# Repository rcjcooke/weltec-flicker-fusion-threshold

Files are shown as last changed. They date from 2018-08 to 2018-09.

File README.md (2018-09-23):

# weltec-flicker-fusion-threshold

Weltec MG7013 Project 0 - Teensy based human flicker fusion threshold determining system.

>"The flicker fusion threshold (or flicker fusion rate) is a concept in the psychophysics of vision. It is defined as the frequency at which an intermittent light stimulus appears to be completely steady to the average human observer."

*Flicker fusion threshold - Wikipedia. (n.d.). Retrieved March 15, 2017, from https://www.wikipedia.com/en/Flicker_fusion_threshold*

The implementation of the system to test this allows the user to adjust a potentiometer to increase or decrease the "flicker rate", the frequency, of an LED blinking on and off. The duty cycle of the flicker is always 50%. The system is designed to allow the user to vary the frequency between 25 and 100 Hz. When the user has determine the point at which they can *just* see a steady state of the LED a button is pressed which tells the user the frequency over a serial interface (USB: 115200 / 8N1).

## Design / Assembly
The design process itself was simple. From a hardware perspective it was clear what was required and from a software perspective it was simply a case of pulling together some button debouncing code, some ADC access code and using the system timer to drive the LED output frequency.  

### Components / BoM
| Supplier | Supplier Part # | # | Description       | MNF Part # |
|:---------|:---------------:|---|:------------------|:-----------|
|          |                 | 1 | Teensy 3.2        |            |
|          |                 | 1 | LED               |            |
|          |                 | 1 | 10k Potentiometer |            |
|          |                 | 1 | 330Ohm Resistor   |            |

**Note**: 330Ohm resistor for current limiting the LED. The Teensy supplies 3.3V on its GPIO pins and allows a maximum current draw of 25mA (ST Microelectronics, 2016). The LED is an unknown quantity so the max forward current is unknown as is it's voltage drop. Based on an assumed voltage drop of 2V (given it's a green LED), R = (Vs - Vf) / I = (3.3-2)/0.025 = 52 Ohms. But given we don't actually know, let's assume no voltage drop across the LED then this would give us 132 Ohm. A safety (and what was available in the box :) ) leaves us with a 330 Ohm resistor.

### Electronics
The components were wired up on breadboard as per the diagram below.

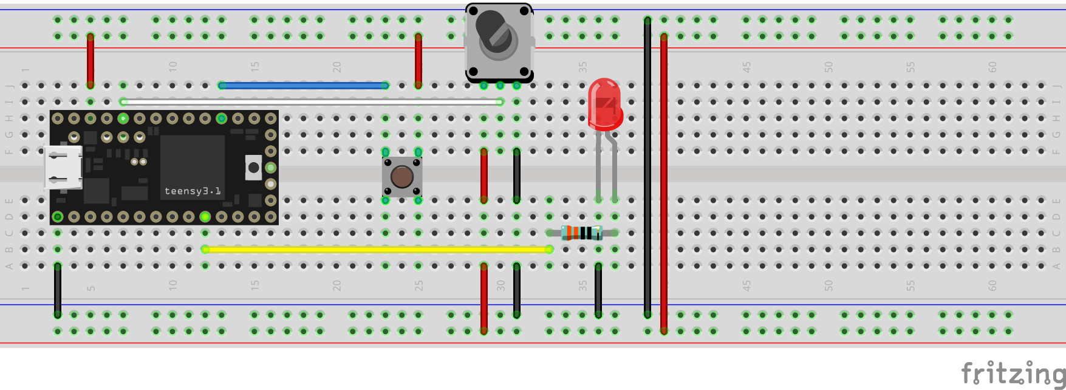
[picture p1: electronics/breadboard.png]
Breadboard image


**Note**: It would appear that Fritzing's Teensy package has the VIN and 3.3V pins switched which is particularly frustrating when trying to get the schematic put together correctly. This is my first time using Fritzing so I haven't investigated this further.

The schematic was drawn up in Eagle as follows:

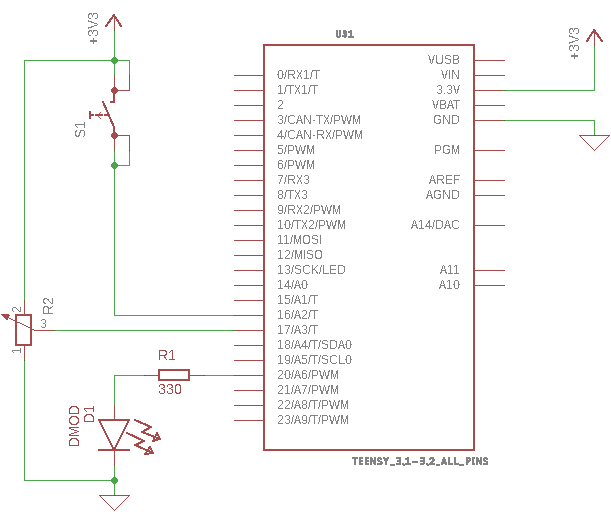
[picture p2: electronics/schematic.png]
Schematic image


### Software

The code has been written to work with the Teensy 3.2 Arduino framework. This is slightly upgraded from the standard Arduino framework and provides "fast" versions of digitalRead for example. This has been taken advantage of on writing the interrupt routine that handles button presses so as not to significantly impede the execution of the interrupt routine which implements a software debounce of the button.

For interest the codebase was also adapted to work on the ESP32 Arduino framework so that debug facilities could be tested on the ESP32 Wrover Kit development board. There are again some subtle variations for the ESP32 implementation of the Arduino framework and these required the addition of a number of preprocessor directives to handle them.

**Note**: The default in platformio.ini is currently set to Teensy. Simply replace the `env_default = teensy31` with `env_default = esp-wrover-kit` to change the default to build and deploy to the ESP32 board instead.

## Results

Serial output looks like the following:

`Flicker fusion threshold frequency: 52.95Hz`<br>
`Flicker fusion threshold frequency: 52.95Hz`<br>
`Flicker fusion threshold frequency: 89.51Hz`<br>
`Flicker fusion threshold frequency: 37.93Hz`<br>
`Flicker fusion threshold frequency: 25.00Hz`<br>
`Flicker fusion threshold frequency: 100.00Hz`<br>
`Flicker fusion threshold frequency: 44.29Hz`<br>
`Flicker fusion threshold frequency: 48.72Hz`<br>

As can be seen, the frequency varies between 25 Hz and 100 Hz.

The calculated frequency output was tested against reality and found to be accurate to within ~0.2Hz. This can be seen in the oscillogram below:

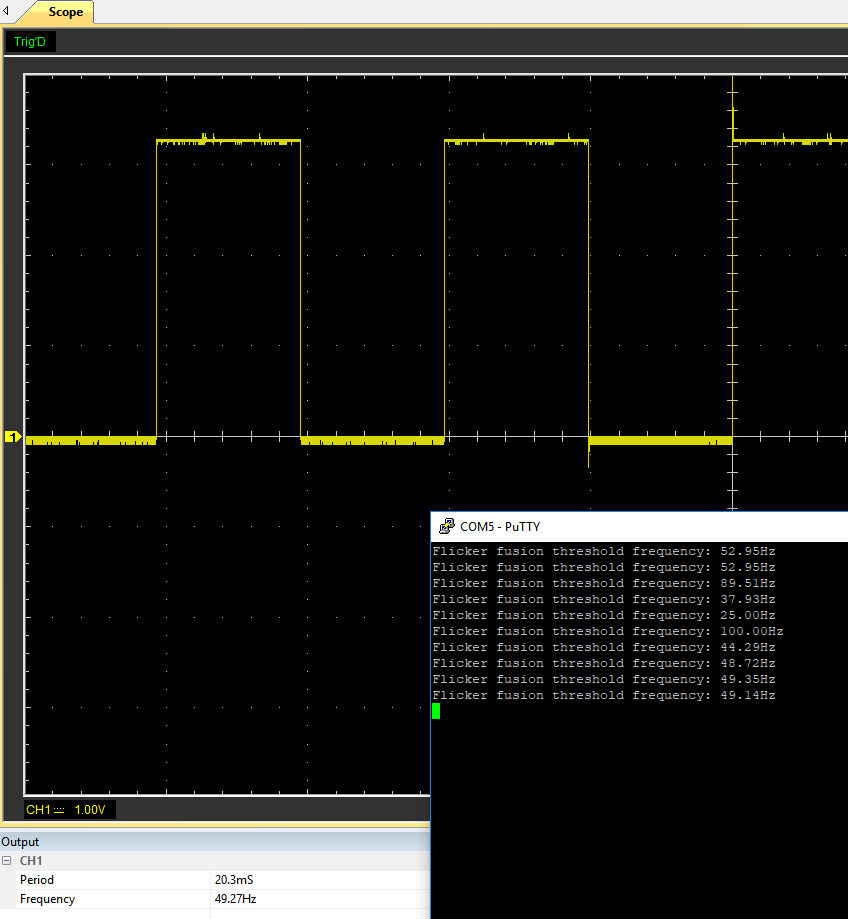
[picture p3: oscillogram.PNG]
LED frequency oscillogram


## Conclusions
It turns out that my threshold is between about 49 and 53 Hz depending on ambient lighting conditions and how directly I'm looking at the LED. Interestingly, I believe it might be lower with a blue LED which I was experimenting with on the ESP32. Further investigation into whether the wavelength affects this phenomenon is warranted given further time.

Given the realisation that ambient lighting conditions have some affect, future experiments should be conducted in a consistently lit, probably dark, environment.

## Update
Since the first cut of this I have also rebuilt this on an ESP Wrover Kit (based on the ESP32 Wroom chip) and added a 7-segment display to show the frequency so that the user doesn't have to fire up a Terminal to find out. The resulting setup can be seen below:

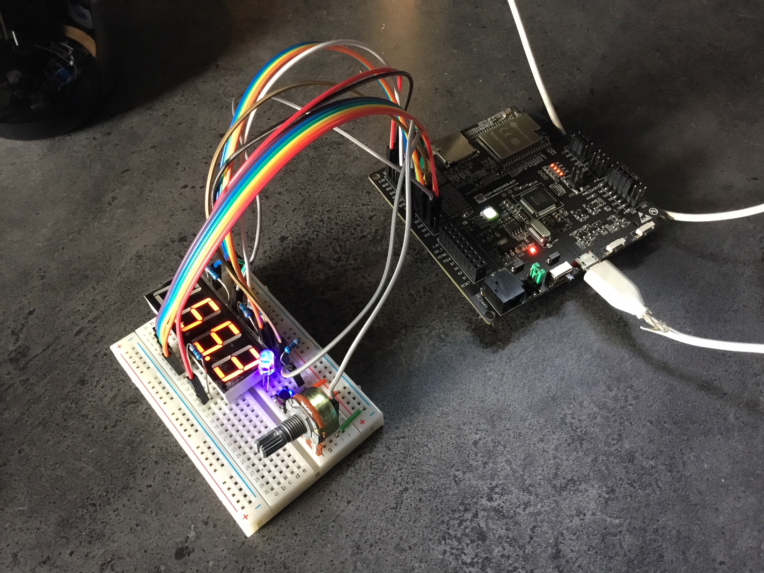
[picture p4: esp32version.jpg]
ESP Wrover Kit based implementation


In putting this together I found a frustrating lack of consolidated information about the ESP Wrover Kit board pinout so I've created a pinout map for it which can be found in the datasheets directory. I couldn't connect up one of the pins for the 4 digit 7-segment display in the end because I didn't have enough GPIO available with the setup that the wrover kit dev board uses (though in theory it's alterable with a little surgery). Also this is because I wanted the JTAG interface available, which steals some additional GPIO when it's enabled. Another couple of pins are used by the 32 KHz crystal on the board. Finally some are input only. Details can be found in the spreadsheet.

Secondly the button I used happen to be WAY more bouncy than the one I used on the Teensy so I had to increase the lockout to 100 ms (instead of only 2ms!). Works nicely now though. There are a number of other quirks of the Arduino framework implementation of the ESP32 I discovered along the way, which can be found in the codebase.

## References

**Note**: Some relevent datasheets can be found in the datasheets directory of this repository.

1. PJRC. (2018, August 24). Teensy 3.2 & 3.1: New Features. Retrieved from pjrc.com: https://www.pjrc.com/teensy/teensy31.html#specs
2. ST Microelectronics. (2016, September). STM32F415xx datasheet - production data; ARM Cortex-M4 32b MCU+FPU, 210DMIPS, up to 1MB Flash/192+4KB RAM, crypto, USB OTG HS/FS, Ethernet, 17 TIMs, 3 ADCs, 15 comm. interfaces & camera.

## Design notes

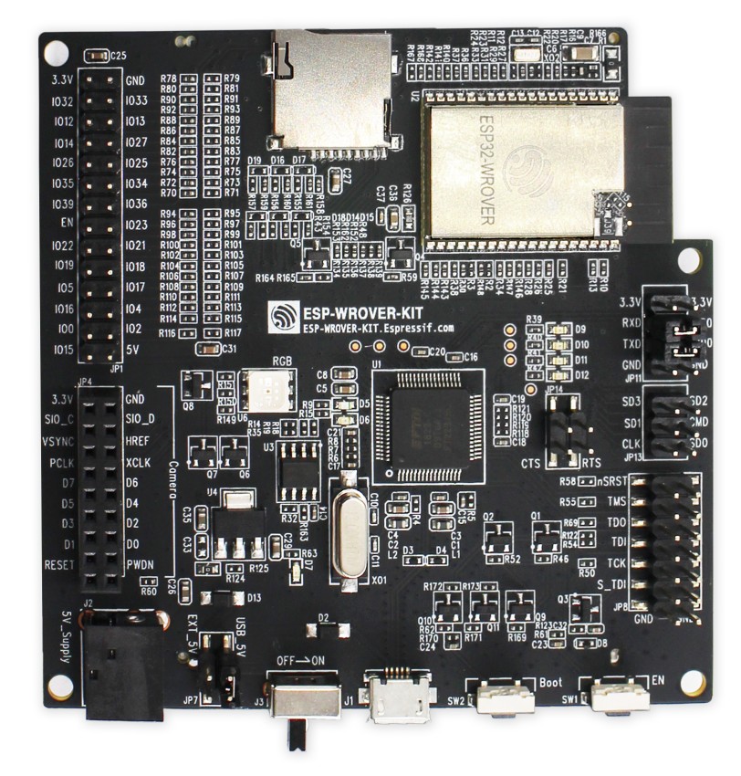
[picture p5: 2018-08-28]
datasheets/esp-wrover-kit-v3.jpg

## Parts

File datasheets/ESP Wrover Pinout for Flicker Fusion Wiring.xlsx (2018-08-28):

 |  |  |  |  |  |  |  |  |  |  |  | # = Number
 |  |  |  |  |  |  |  |  |  |  |  | T = Type |  | SPI01 | SPI2 | SPI3
 |  |  |  |  |  |  |  |  |  |  |  | GPIO | RTC GPIO | DAC
 |  |  |  |  |  |  |  |  |  |  |  | ADC1 | ADC2 | EMAC
 |  |  |  |  |  |  |  |  |  |  |  | TOUCH |  | SDIO Slave
 |  |  |  |  |  |  |  |  |  |  |  | Clock |  | SDIO Host Port 1 | SDIO Host Port 2
 |  |  |  |  |  |  |  |  |  |  |  |  |  | JTAG
 |  |  |  |  |  |  |  |  |  |  |  |  |  | UART0 | UART1 | UART2
 |  | T | # | Name | Silk | Silk | Name | # | T
 |  | P | 2 | 3V3 | 3.3V | GND | GND | 1 | P
 | XTAL_32K_P | I/O | 8 | IO32 | IO32 | IO33 | IO33 | 9 | I/O | XTAL_32K_N
 | MTDI | I/O | 14 | IO12 | IO12 | IO13 | IO13 | 16 | I/O | MTCK
 | MTMS | I/O | 13 | IO14 | IO14 | IO27 | IO27 | 12 | I/O | GPIO27 | 7-Seg-Display E
7-Seg-Display B | GPIO26 | I/O | 11 | IO26 | IO26 | IO25 | IO25 | 10 | I/O | GPIO25 | 7-Seg-Display D
 |  | I | 7 | IO35 | IO35 | IO34 | IO34 | 6 | I | GPIO34 | Button input pin
 |  | I | 5 | SENSOR_VN | IO39 | IO36 | SENSOR_VP | 4 | I | ADC1_CH0 | Potentiometer input pin
 |  | I | 3 | EN | EN | IO23 | IO23 | 37 | I/O | GPIO23 | 7-Seg-Display DP
7-Seg-Display A | GPIO22 | I/O | 36 | IO22 | IO22 | IO21 | IO21 | 33 | I/O | GPIO21 | 7-Seg-Display C
7-Seg-Display 2 | GPIO19 | I/O | 31 | IO19 | IO19 | IO18 | IO18 | 30 | I/O | GPIO18 | LED output pin
7-Seg-Display 3 | GPIO5 | I/O | 29 | IO5 | IO5 | IO17 | Connected to Integrated PSRAM
 |  |  |  | Connected to Integrated PSRAM | IO16 | IO4 | IO4 | 26 | I/O | GPIO4 | 7-Seg-Display G
7-Seg-Display F |  | I/O | 25 | IO0 | IO0 | IO2 | IO2 | 24 | I/O | GPIO2 | 7-Seg-Display 4
 | MTDO | I/O | 23 | IO15 | IO15 | 5V
 |  |  |  |  | JP1

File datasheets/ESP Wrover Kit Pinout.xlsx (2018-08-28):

 |  |  |  |  |  |  |  |  |  |  |  |  |  |  |  |  |  |  |  |  |  |  |  |  |  | # = Number
 |  |  |  |  |  |  |  |  |  |  |  |  |  |  |  |  |  |  |  |  |  |  |  |  |  | T = Type |  | SPI01 | SPI2 | SPI3
 |  |  |  |  |  |  |  |  |  |  |  |  |  |  |  |  |  |  |  |  |  |  |  |  |  | GPIO | RTC GPIO | DAC
 |  |  |  |  |  |  |  |  |  |  |  |  |  |  |  |  |  |  |  |  |  |  |  |  |  | ADC1 | ADC2 | EMAC
 |  |  |  |  |  |  |  |  |  |  |  |  |  |  |  |  |  |  |  |  |  |  |  |  |  | TOUCH |  | SDIO Slave
 |  |  |  |  |  |  |  |  |  |  |  |  |  |  |  |  |  |  |  |  |  |  |  |  |  | Clock |  | SDIO Host Port 1 | SDIO Host Port 2
 |  |  |  |  |  |  |  |  |  |  |  |  |  |  |  |  |  |  |  |  |  |  |  |  |  |  |  | JTAG
 |  |  |  |  |  |  |  |  |  |  |  |  |  |  |  |  |  |  |  |  |  |  |  |  |  |  |  | UART0 | UART1 | UART2
 |  |  |  |  |  |  |  |  | T | # | Name | Silk | Silk | Name | # | T
 |  |  |  |  |  |  |  |  | P | 2 | 3V3 | 3.3V | GND | GND | 1 | P
 |  |  |  | XTAL_32K_P | TOUCH9 | ADC1_CH4 | RTC_GPIO9 | GPIO32 | I/O | 8 | IO32 | IO32 | IO33 | IO33 | 9 | I/O | GPIO33 | RTC_GPIO8 | ADC1_CH5 | TOUCH8 | XTAL_32K_N
MTDI | SD_DATA2 | HS2_DATA2 | HSPIQ | EMAX_TXD3 | TOUCH5 | ADC2_CH5 | RTC_GPIO15 | GPIO12 | I/O | 14 | IO12 | IO12 | IO13 | IO13 | 16 | I/O | GPIO13 | RTC_GPIO14 | ADC2_CH4 | TOUCH4 | EMAC_RX_ER | HSPID | HS2_DATA3 | SD_DATA3 | MTCK
MTMS | SD_CLK | HS2_CLK | HSPICLK | EMAX_TXD2 | TOUCH6 | ADC2_CH6 | RTC_GPIO16 | GPIO14 | I/O | 13 | IO14 | IO14 | IO27 | IO27 | 12 | I/O | GPIO27 | RTC_GPIO17 | ADC2_CH7 | TOUCH7 | EMAC_RX_DV
 |  |  |  | EMAC_RXD1 | DAC_2 | ADC2_CH9 | RTC_GPIO7 | GPIO26 | I/O | 11 | IO26 | IO26 | IO25 | IO25 | 10 | I/O | GPIO25 | RTC_GPIO6 | ADC2_CH8 | DAC_1 | EMAC_RXD0
 |  |  |  |  |  | ADC1_CH7 | RTC_GPIO5 | GPIO35 | I | 7 | IO35 | IO35 | IO34 | IO34 | 6 | I | GPIO34 | RTC_GPIO4 | ADC1_CH6
 |  |  |  |  |  | ADC1_CH3 | RTC_GPIO3 | GPIO39 | I | 5 | SENSOR_VN | IO39 | IO36 | SENSOR_VP | 4 | I | GPIO36 | RTC_GPIO0 | ADC1_CH0
 |  |  |  |  |  |  |  |  | I | 3 | EN | EN | IO23 | IO23 | 37 | I/O | GPIO23 |  |  |  |  | VSPID | HS1_STROBE
 |  |  | VSPIWP | EMAC_TXD1 |  |  | U0RTS | GPIO22 | I/O | 36 | IO22 | IO22 | IO21 | IO21 | 33 | I/O | GPIO21 |  |  |  | EMAC_TX_EN | VSPIHD
 |  |  | VSPIQ | EMAC_TXD0 |  |  | U0CTS | GPIO19 | I/O | 31 | IO19 | IO19 | IO18 | IO18 | 30 | I/O | GPIO18 |  |  |  |  | VSPICLK | HS1_DATA7
 |  | HS1_DATA6 | VSPICS0 | EMAC_RX_CLK |  |  |  | GPIO5 | I/O | 29 | IO5 | IO5 | IO17 | Connected to Integrated PSRAM
 |  |  |  |  |  |  |  |  |  |  | Connected to Integrated PSRAM | IO16 | IO4 | IO4 | 26 | I/O | GPIO4 | RTC_GPIO10 | ADC2_CH0 | TOUCH0 | EMAC_TX_ER | HSPIHD | HS2_DATA1 | SD_DATA1
 |  |  | CLK_OUT1 | EMAC_TX_CLK | TOUCH1 | ADC2_CH1 | RTC_GPIO11 | GPIO0 | I/O | 25 | IO0 | IO0 | IO2 | IO2 | 24 | I/O | GPIO2 | RTC_GPIO12 | ADC2_CH2 | TOUCH2 |  | HSPIWP | HS2_DATA0 | SD_DATA0
MTDO | SD_CMD | HS2_CMD | HSPICS0 | EMAC_RXD3 | TOUCH3 | ADC2_CH3 | RTC_GPIO13 | GPIO15 | I/O | 23 | IO15 | IO15 | 5V
 |  |  |  |  |  |  |  |  |  |  |  | JP1
 |  |  |  |  |  |  |  |  |  |  |  | 3.3V | GND
 |  |  |  |  |  |  |  |  |  |  |  | SIO_C | SIO_D
 |  |  |  |  |  |  |  |  |  |  |  | VSYNC | HREF
 |  |  |  |  |  |  |  |  |  |  |  | PCLK | XCLK
 |  |  |  |  |  |  |  |  |  |  |  | D7 | D6
 |  |  |  |  |  |  |  |  |  |  |  | D5 | D4
 |  |  |  |  |  |  |  |  |  |  |  | D3 | D2
 |  |  |  |  |  |  |  |  |  |  |  | D1 | D0
 |  |  |  |  |  |  |  |  |  |  |  | RESET | PWDN
 |  |  |  |  |  |  |  |  |  |  |  | JP4
 |  |  |  |  |  |  |  |  |  |  |  | 3.3V | 3.3V
 |  |  |  |  |  |  |  |  |  |  |  | RXD | TXD0 | TXD0 | 35 | I/O | GPIO1 | CLK_OUT3 |  | EMAC_RXD2 | U0TXD
 |  |  |  |  |  |  |  |  |  |  |  | TXD | RXD0 | RXD0 | 34 | I/O | GPIO3 | CLK_OUT2 |  |  | U0RXD
 |  |  |  |  |  |  |  |  |  |  |  | GND | GND
 |  |  |  |  |  |  |  |  |  |  |  | JP11
 |  |  |  | U1TXD | HS1_DATA3 | SPIWP | SD_DATA3 | GPIO10 | I/O | 18 | SWP/SD3 | SD3 | SD2 | SHD/SD2 | 17 | I/O | GPIO9 | SD_DATA2 | SPIHD | HS1_DATA2 | U1RXD
 |  |  |  | U2CTS | HS1_DATA1 | SPID | SD_DATA1 | GPIO8 | I/O | 22 | SDI/SD1 | SD1 | CMD | SCS/CMD | 19 | I/O | GPIO11 | SD_CMD | SPICS0 | HS1_CMD | U1RTS
 |  |  |  | U1CTS | HS1_CLK | SPICLK | SD_CLK | GPIO6 | I/O | 20 | SCK/CLK | CLK | SD0 | SDO/SD0 | 21 | I/O | GPIO7 | SD_DATA0 | SPIQ | HS1_DATA0 | U2RTS
 |  |  |  |  |  |  |  |  |  |  |  | JP13

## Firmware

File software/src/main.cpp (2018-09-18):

#include <Arduino.h>
#include <SevSeg.h>

// Surprised this definition doesn't exist in the ESP IDF
#define ADC1_CH0 36

/************************
 * Constants
 ************************/
// Pin definitions
#if ESP_PLATFORM
  static const uint8_t LED_PIN = 18;
  static const uint8_t POTENTIOMETER_PIN = ADC1_CH0;
  static const uint8_t BUTTON_PIN = 34;
#else
  static const uint8_t LED_PIN = 18;
  static const uint8_t POTENTIOMETER_PIN = A3;
  static const uint8_t BUTTON_PIN = 16;
#endif // ESP_PLATFORM
// For 7-Segment Display Pinout see:
// http://haneefputtur.com/7-segment-4-digit-led-display-sma420564-using-arduino.html
// Note: Can't use pin 32 at the moment so first digit is physically unconnected
// as 32 is assigned to 32KHz crystal on the Wrover Kit board.
static const uint8_t DISPLAY_1_PIN = 32;
static const uint8_t DISPLAY_2_PIN = 19;
static const uint8_t DISPLAY_3_PIN = 5;
static const uint8_t DISPLAY_4_PIN = 2;
static const uint8_t DISPLAY_A_PIN = 22;
static const uint8_t DISPLAY_B_PIN = 26;
static const uint8_t DISPLAY_C_PIN = 21;
static const uint8_t DISPLAY_D_PIN = 25;
static const uint8_t DISPLAY_E_PIN = 27;
static const uint8_t DISPLAY_F_PIN = 0;
static const uint8_t DISPLAY_G_PIN = 4;
static const uint8_t DISPLAY_DP_PIN = 23;

// Delay before accepting button state change for debouncing purposes
static const unsigned long LOCKOUT_DELAY_MILLIS = 100;

// The minimum period of time for which the LED will blink on in microseconds
static const unsigned long MIN_HALF_PERIOD_MICROS = 5000;
// The maximum period of time for which the LED will blink on in microseconds
static const unsigned long MAX_HALF_PERIOD_MICROS = 20000;

/************************
 * Variables
 ************************/
// True if the button has been pressed but not actioned
volatile bool gButtonStateChangeToAction = false;
// The debounced button state
uint8_t gButtonState = LOW;

// The time in microseconds that the LED is currently on or off
unsigned long gHalfPeriod = 100000;
// The last time we changed the state of the LED in system microseconds
unsigned long gLastLEDChangeMicros = 0;
// The current state of the LED
uint8_t gLEDState = LOW;
// Seven Segment display instance
SevSeg mSevenSegmentDisplay;

/*********************
 * Interrupt routines
 *********************/
#if ESP_PLATFORM
// ESP32 ISR Handlers MUST be placed in IRAM
// (https://esp-idf.readthedocs.io/en/v2.0/general-notes.html#iram-instruction-ram)
void IRAM_ATTR buttonPressedISR() {
#else
void buttonPressedISR() {
#endif // ESP_PLATFORM
  unsigned long currentMillis = millis();
  cli();
  static unsigned long lastButtonStateChangeTime = 0;

#if ESP_PLATFORM
  uint8_t newButtonState = digitalRead(BUTTON_PIN);
#else
  uint8_t newButtonState = digitalReadFast(BUTTON_PIN);
#endif // ESP_PLATFORM

  // Make sure we're not in the lockout period
  if (currentMillis - lastButtonStateChangeTime > LOCKOUT_DELAY_MILLIS) {
    // Only do anything if we've changed state
    if (gButtonState != newButtonState) {
      lastButtonStateChangeTime = currentMillis;
      gButtonStateChangeToAction = true;
      gButtonState = newButtonState;
    }
  }
  sei();
}

/*********************
 * Entry Point methods
 *********************/
// Setup function - executes once on startup
void setup() {
  // Set up pins and internals
  pinMode(LED_PIN, OUTPUT);
  pinMode(BUTTON_PIN, INPUT_PULLDOWN);
  pinMode(POTENTIOMETER_PIN, INPUT);
  analogReadResolution(10);
#if ESP_PLATFORM
  analogSetAttenuation(ADC_6db);
#endif // ESP_PLATFORM
  byte numDigits = 4;
  byte digitPins[] = {DISPLAY_1_PIN, DISPLAY_2_PIN, DISPLAY_3_PIN,
                      DISPLAY_4_PIN};
  byte segmentPins[] = {DISPLAY_A_PIN, DISPLAY_B_PIN, DISPLAY_C_PIN,
                        DISPLAY_D_PIN, DISPLAY_E_PIN, DISPLAY_F_PIN,
                        DISPLAY_G_PIN, DISPLAY_DP_PIN};
  mSevenSegmentDisplay.begin(COMMON_CATHODE, numDigits, digitPins, segmentPins, true);

  attachInterrupt(digitalPinToInterrupt(BUTTON_PIN), buttonPressedISR, CHANGE);
  digitalWrite(LED_PIN, gLEDState);
  Serial.begin(115200);
}

// Loop function - loops :)
void loop() {
  // Flash the LED
  unsigned long curMicros = micros();
  if (curMicros - gLastLEDChangeMicros > gHalfPeriod) {
    gLEDState = !gLEDState;
    digitalWrite(LED_PIN, gLEDState);
    gLastLEDChangeMicros = curMicros;
  }

  // Check the potentiometer
  int rawPotValue = analogRead(POTENTIOMETER_PIN);

#if ESP_PLATFORM
  gHalfPeriod = map((long)rawPotValue, 0, 1023, (long)MIN_HALF_PERIOD_MICROS,
                    (long)MAX_HALF_PERIOD_MICROS);
#else
  gHalfPeriod = map<int, int, int, unsigned long, unsigned long>(
      rawPotValue, 0, 1023, MIN_HALF_PERIOD_MICROS, MAX_HALF_PERIOD_MICROS);
#endif // ESP_PLATFORM

  // Check to see if the user has pressed the button
  if (gButtonStateChangeToAction && gButtonState == HIGH) {
    // Print current frequency
    float frequency = (float)500000 / ((float)gHalfPeriod);
    Serial.println("Flicker fusion threshold frequency: " + String(frequency) +
                   "Hz");
    mSevenSegmentDisplay.setNumber(frequency, 1);
    gButtonStateChangeToAction = false;
  }
  mSevenSegmentDisplay.refreshDisplay();
}

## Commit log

2018-08-21 first cut implementation
    [breadboard.fzz, schematic.sch]
2018-08-24 Added esp32 platform for debugging purposes
2018-08-24 Getting it working on ESP32 Wrover Kit
2018-08-24 Fixed Teensy bug introduced when I added ESP32
2018-08-28 Added ESP32 version with 7-segment display
    [ESP Wrover Kit Pinout.xlsx, ESP Wrover Pinout for Flicker Fusion Wiring.xlsx]
